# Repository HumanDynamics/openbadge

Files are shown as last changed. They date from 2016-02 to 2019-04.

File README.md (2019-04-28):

# OpenBadge project #

Welcome to the Open Badge project, an open-source framework and toolkit for measuring and shaping face-to-face social interactions using either custom hardware devices or smart phones, and real-time web-based visualizations. Open Badges is a modular system that allows researchers to monitor and collect interaction data from people engaged in real-life social settings. For more information, please read our main publications ([1](https://ieeexplore.ieee.org/document/8259434),[2](https://www.media.mit.edu/publications/rhythm-a-unified-measurement-platform-for-human-organizations/),[3](https://www.media.mit.edu/publications/open-badges-a-low-cost-toolkit-for-measuring-team-communication-and-dynamics/)) ,visit our [wiki](https://github.com/HumanDynamics/OpenBadge/wiki), or join our [discussion forum](https://groups.google.com/d/forum/rhythm-badges).

Additional repositories that are part of this project:
* https://github.com/mitmedialab/rhythm-badge-programmer - schematics, vector files and instructions for making a programming rig 

* https://github.com/HumanDynamics/openbadge-hub-py - a python based hub (base station) for pulling data from badges

* https://github.com/HumanDynamics/openbadge-hub - a Javascript/Cordova app that communicates with the badges and stores
 the data to a server
* https://github.com/HumanDynamics/openbadge-server - the backend server for the app

* https://github.com/HumanDynamics/openbadge-analysis - Python (2.7) package for loading and pre-processing badge data

* https://github.com/HumanDynamics/openbadge-analysis-examples - Examples showing how to use the analysis package

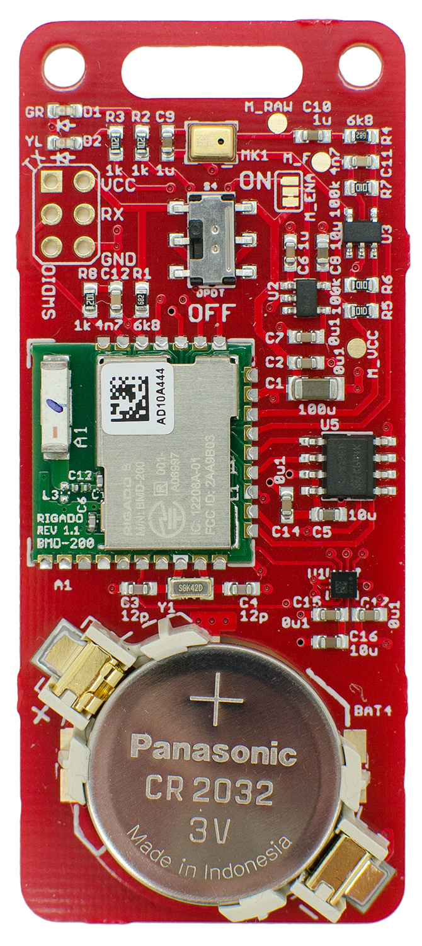
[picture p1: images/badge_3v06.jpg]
Badge Open Badge


## Docker wrapper ##
The nRF working environment is now available as a Docker container. The following commands have been tested under Ubuntu
linux, but should work under iOS as well (with some modifications, especially to the device names).

Important notes:
1. The badge must be connected to the programmer before starting the docker (using docker-compose run)
2. Docker will mount the project directory under /app inside the container, so the container can see the latest changes
 (no need to build the container after every code change)

Commands:
* docker-compose build : builds the docker container "nrf". You must run this command at least once before calling
 docker-compose run.
* docker-compose run nrf <COMMAND> : where <COMMAND> is a command to run inside the container.
  * When calling make (e.g. make badge_03v6_noDebug flashUnlock flashErase  flashS130 flashAPP), the script will automatically
  change the working directory to the data_collector directory. You can see the different make options by calling:
  "docker-compose run nrf make"
* docker-compose run nrf bash : opens an interactive bash shell
* ./programming_loop_docker.sh [test/prod] : a utility used for programming a batch of badges. It will compile once, and
 then enters a loop. Each time a new badge is placed, it will be automatically programmed and its MAC address will be
 written to the macs.log file. For most purposes, use the "prod" command variables. The "test" option turns on serial
 output and other testing features and is not recommended for production.

If you are using a raspberry pi to run this code, please use the raspberry pi compose file (-f docker-compose-raspi.yml). For example `docker-compose -f docker-compose-raspi.yml build`.

## Firmware testing tools ##
The framework includes two tools for testing firmware code
* Badge terminal. The utility opens a connections to a badge and allows you to run simple commands. To run, use the following docker command: `docker-compose run nrf terminal <MAC ADDRESS>`
* Integration tests. These are tests designed for testing basic badge functionality. To run the tests, use the following docker command: `docker-compose run nrf run_all_tests <MAC ADDRESS>`

Note that in order to run the integration tests, you'll need to have a badge connected with a serial interface. A regular J-Link debugger/programmer does not include these. We recommend using a nRF51 dev-kit as a programmer for this purpose (see our wiki/documentations on how to make one).

## Badge testing procedure ##
The badge firmware includes a tester mode that can be used for testing new badges. 
To compile, use the badge_03v6_tester flag (or badge_03v4_tester, for older hardware). For example:
```
make badge_03v6_noDebug flashUnlock flashErase  flashS130 flashAPP
```

Or, when using docker:
```
docker-compose run nrf make badge_03v6_noDebug flashUnlock flashErase  flashS130 flashAPP
```

Once programmed, the badge uses the LEDs to indicate the status of the test:
1. Blink red LED several times, one for each test (EEPROM, Flash, etc)
2. Microphone test. When it starts, both green and red LEDs will turn on 
It then looks for quiet->noise->quiet->noise pattern, each section must be at least 200 ms long. 
This must be completed within 10 seconds.
In a quiet place, simply say "ahhhh" twice, with pause in between. Every time the noise passed the threshold, the LEDs 
will turn off
3. Accelerometer test. When it starts, both green and red LEDs will turn on. Simply shake the badge
4. Once done, the green LED will turn off for several seconds and then turn off

Example for known issues with badge manufacturing:
* LEDs not turning on - might be a problem with the LEDs themselves
* When microphone test starts, both LEDs will momentarily turn on and then off
This might indicate a problem in the microphone filter or amplifier circuit (the microphone saturates and noise level says high)

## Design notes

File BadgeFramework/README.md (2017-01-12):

#BadgeFramework

This is a basic set of frameworks and libraries that are useful for interfacing with the badge in Python.

We currently have:

- BadgeConnection: An interface for an implementation of a badge communication layer.
- BLEBadgeConnection: An implementation of BadgeConnection that communicates with the badge over BLE using the Adafruit Bluefruit library.
- Badge: An object that communicates with a badge using the BadgeConnection
- badge_protocol: A set of BadgeMessage objects that make it easy to define, serialize, and deserialize the badge's proprietery binary communication messages.

We also include an example development terminal *terminal.py* that illustrates how one can use these various components to communicate with the badge. 

To try out the terminal, you must first install the [Adafruit Bluefruit library](https://github.com/adafruit/Adafruit_Python_BluefruitLE), and then simply run `python terminal.py` in this directory.

The purpose of this library is to expedite development of many tools (hub, integration test, developer terminal, etc.) that all have to communicate with the badge by forming a common, reusable codebase that all of these tools can use. As such, the framework is designed to be modular.  (E.g. the only portion of this framework that depends on a specific BLE library is BLEBadgeConnection, and one can easily swap out BadgeConnection implementations for say one that uses UART, or one can easily import the badge_protocol definitions into a different project)

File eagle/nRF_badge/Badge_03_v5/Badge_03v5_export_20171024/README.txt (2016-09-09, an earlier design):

Exported using PCB.ng CAM file
pnp_bom.txt file was created using the combine.py script and then cleaned up manually

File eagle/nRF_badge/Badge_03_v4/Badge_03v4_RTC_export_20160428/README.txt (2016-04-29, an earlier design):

In these files I manually fix the following issues i nthe BOM:
* C12 should be 4.7nF
* U4 should be 568-12405-1-ND 
* BAT1 should be BK-912-CT-ND (cut-tape)

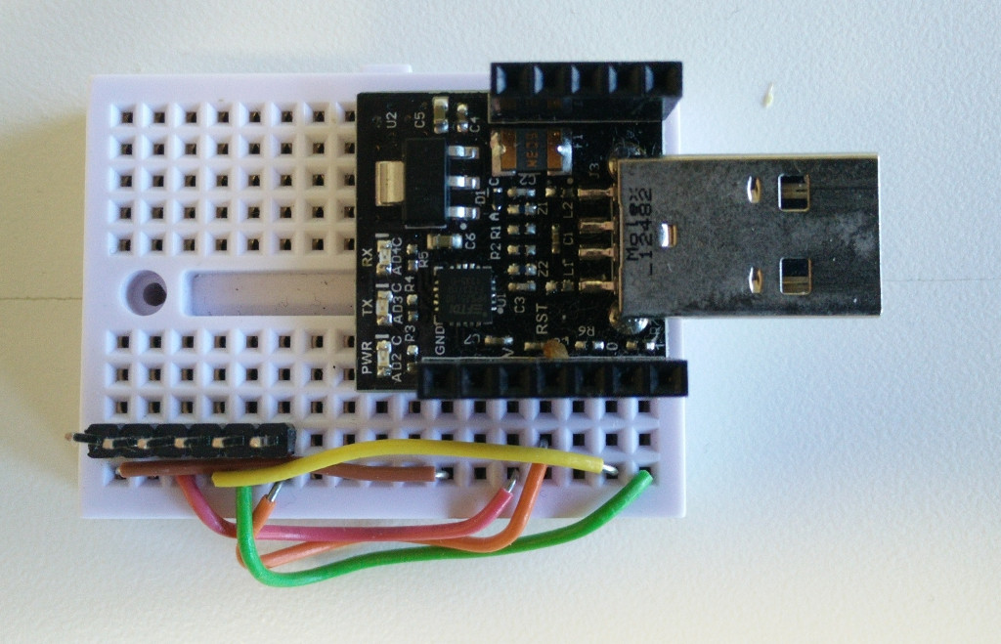
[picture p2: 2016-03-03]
images/v2_programmer.jpg

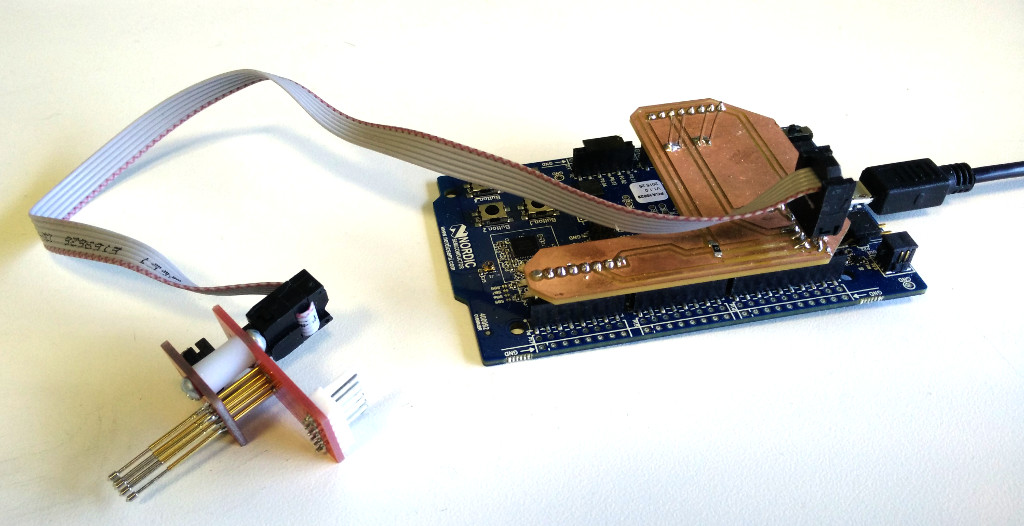
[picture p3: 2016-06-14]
images/programmer_v3.jpg

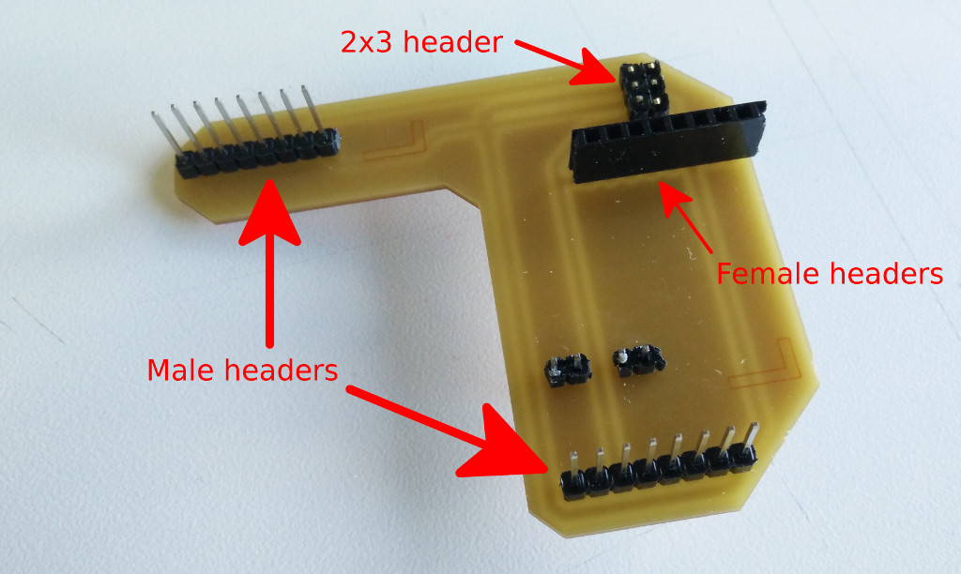
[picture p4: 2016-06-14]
images/programmer_v3_bottom.jpg

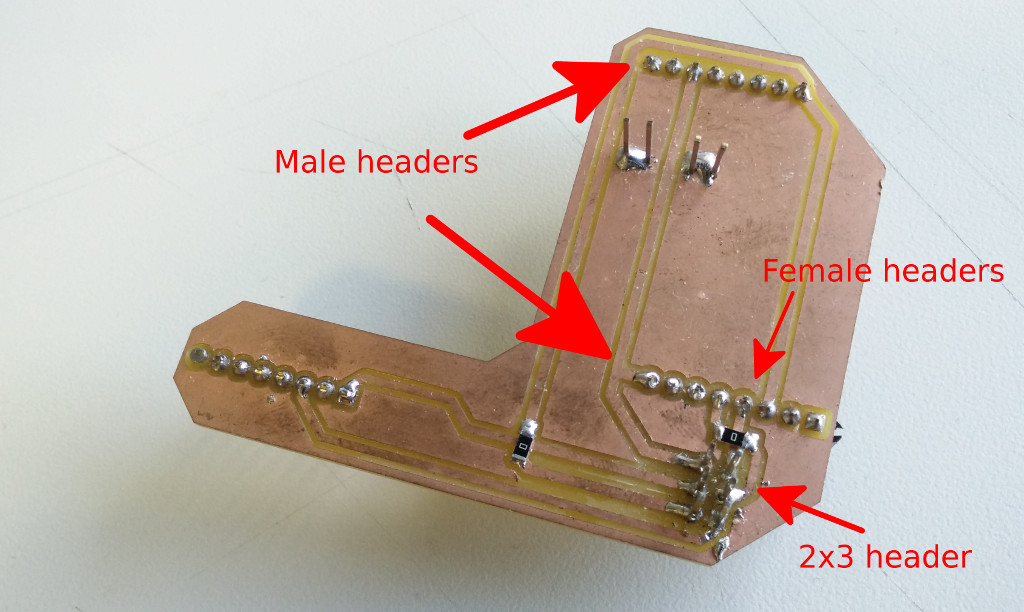
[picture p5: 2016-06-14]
images/programmer_v3_top.jpg

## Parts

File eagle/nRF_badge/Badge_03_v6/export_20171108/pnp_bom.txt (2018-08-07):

SMD component position file.
Centroid Data for pc board: "badge_03v6.brd" as of: 11/8/17 3:46 PM
Measurements are in mm. Comma delimited
Only surface mount components included

RefDes,LocationX,LocationY,Rotation,Layer,DigiKey
A1,9.500,36.500,90,Top,1604-1004-1-ND
BAT4,15.000,12.250,323,Top,BU2032SM-BT-GCT-ND
C1,23.000,41.500,0,Top,490-4539-1-ND
C2,22.250,43.500,0,Top,490-1532-1-ND
C3,9.250,26.000,180,Top,490-1405-1-ND
C4,17.250,26.000,0,Top,490-1405-1-ND
C5,24.000,31.750,0,Top,490-6405-1-ND
C6,21.000,52.000,90,Top,490-1543-1-ND
C7,22.250,45.500,0,Top,490-1532-1-ND
C8,23.500,52.000,90,Top,490-6405-1-ND
C9,11.500,60.500,90,Top,490-1543-1-ND
C10,22.750,61.000,0,Top,490-1543-1-ND
C11,26.500,59.000,180,Top,1276-1098-1-ND
C12,7.500,48.375,270,Top,1276-1098-1-ND
C14,20.750,32.500,90,Top,490-1532-1-ND
C15,27.250,26.000,0,Top,490-1532-1-ND
C16,26.000,28.125,0,Top,490-6405-1-ND
C17,24.250,26.000,180,Top,490-1532-1-ND
D1,3.500,63.000,0,Top,475-2709-1-ND
D2,3.500,60.500,0,Top,475-2712-1-ND
MK1,15.000,60.500,180,Top,423-1134-1-ND
R1,9.500,48.375,90,Top,RMCF0603JT6K80CT-ND
R2,9.500,60.500,270,Top,311-1.0KGRCT-ND
R3,7.500,60.500,270,Top,311-1.0KGRCT-ND
R4,26.500,61.000,180,Top,RMCF0603JT6K80CT-ND
R5,26.500,47.500,0,Top,311-100KGRCT-ND
R6,26.500,49.500,0,Top,311-100KGRCT-ND
R7,26.500,57.000,180,Top,311-100KGRCT-ND
R8,5.500,48.375,90,Top,311-1.0KGRCT-ND
R11,27.500,21.125,0,Top,311-1.0KGRCT-ND
R12,24.375,21.125,180,Top,311-1.0KGRCT-ND
S4,15.000,53.000,270,Top,401-2013-1-ND
U1,25.875,23.625,90,Top,497-14851-1-ND
U2,22.250,48.500,0,Top,296-18474-1-ND
U3,26.500,53.500,90,Top,MCP6231T-E/OTCT-ND
U5,25.500,35.500,180,Top,497-11405-1-ND
Y1,13.250,26.000,180,Top,535-11937-1-ND

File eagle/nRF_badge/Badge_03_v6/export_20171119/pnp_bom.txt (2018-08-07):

SMD component position file.
Centroid Data for pc board: "badge_03v6.brd" as of: 11/19/17 4:50 PM
Measurements are in mm. Comma delimited
Only surface mount components included

RefDes,LocationX,LocationY,Rotation,Layer,DigiKey
A1,9.500,36.500,90,Top,1604-1004-1-ND
BAT4,15.000,12.250,323,Top,BU2032SM-BT-GCT-ND
C1,23.000,41.500,0,Top,490-4539-1-ND
C2,22.250,43.500,0,Top,490-1532-1-ND
C3,9.250,26.000,180,Top,490-1405-1-ND
C4,17.250,26.000,0,Top,490-1405-1-ND
C5,24.000,31.750,0,Top,490-6405-1-ND
C6,21.000,52.000,90,Top,490-1543-1-ND
C7,22.250,45.500,0,Top,490-1532-1-ND
C8,23.500,52.000,90,Top,490-6405-1-ND
C9,11.500,60.500,90,Top,490-1543-1-ND
C10,22.750,61.000,0,Top,490-1543-1-ND
C11,26.500,59.000,180,Top,1276-1098-1-ND
C12,7.500,48.375,270,Top,1276-1098-1-ND
C14,20.750,32.500,90,Top,490-1532-1-ND
C15,24.125,24.000,180,Top,490-1532-1-ND
C16,24.125,21.875,180,Top,490-6405-1-ND
C17,27.125,24.000,0,Top,490-1532-1-ND
D1,3.500,63.000,0,Top,475-2709-1-ND
D2,3.500,60.500,0,Top,475-2712-1-ND
MK1,15.000,60.500,180,Top,423-1134-1-ND
R1,9.500,48.375,90,Top,RMCF0603JT6K80CT-ND
R2,9.500,60.500,270,Top,311-1.0KGRCT-ND
R3,7.500,60.500,270,Top,311-1.0KGRCT-ND
R4,26.500,61.000,180,Top,RMCF0603JT6K80CT-ND
R5,26.500,47.500,0,Top,311-100KGRCT-ND
R6,26.500,49.500,0,Top,311-100KGRCT-ND
R7,26.500,57.000,180,Top,311-100KGRCT-ND
R8,5.500,48.375,90,Top,311-1.0KGRCT-ND
S4,15.000,53.000,270,Top,401-2013-1-ND
U1,25.125,26.375,270,Top,497-14851-1-ND
U2,22.250,48.500,0,Top,296-18474-1-ND
U3,26.500,53.500,90,Top,MCP6231T-E/OTCT-ND
U5,25.500,35.500,180,Top,497-11405-1-ND
Y1,13.250,26.000,180,Top,535-11937-1-ND

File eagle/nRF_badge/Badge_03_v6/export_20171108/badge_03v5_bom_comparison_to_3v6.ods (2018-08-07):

v5 |  |  | v6
Part | Value | Digikey# | Part | Value | Digikey# | save value | same value | same key
A1 | BMD-200 | 1604-1004-1-ND | A1 | BMD-200 | 1604-1004-1-ND | 1 | 1 | 1
BAT4 | CR2032 | BU2032SM-BT-GCT-ND | BAT4 | CR2032 | BU2032SM-BT-GCT-ND | 1 | 1 | 1
C1 | 100u | 490-4539-1-ND | C1 | 100u | 490-4539-1-ND | 1 | 1 | 1
C2 | 0u1 | 490-1532-1-ND | C2 | 0u1 | 490-1532-1-ND | 1 | 1 | 1
C3 | 12p | 490-1405-1-ND | C3 | 12p | 490-1405-1-ND | 1 | 1 | 1
C4 | 12p | 490-1405-1-ND | C4 | 12p | 490-1405-1-ND | 1 | 1 | 1
C5 | 10u | 490-6405-1-ND | C5 | 10u | 490-6405-1-ND | 1 | 1 | 1
C6 | 1u | 490-1543-1-ND | C6 | 1u | 490-1543-1-ND | 1 | 1 | 1
C7 | 0u1 | 490-1532-1-ND | C7 | 0u1 | 490-1532-1-ND | 1 | 1 | 1
C8 | 10u | 490-6405-1-ND | C8 | 10u | 490-6405-1-ND | 1 | 1 | 1
C9 | 1u | 490-1543-1-ND | C9 | 1u | 490-1543-1-ND | 1 | 1 | 1
C10 | 1u | 490-1543-1-ND | C10 | 1u | 490-1543-1-ND | 1 | 1 | 1
C11 | 4n7 | 1276-1098-1-ND | C11 | 4n7 | 1276-1098-1-ND | 1 | 1 | 1
C12 | 4n7 | 1276-1098-1-ND | C12 | 4n7 | 1276-1098-1-ND | 1 | 1 | 1
C13 | 12p | 490-1405-1-ND |  |  |  | 0 | 0 | 0
C14 | 0u1 | 490-1532-1-ND | C14 | 0u1 | 490-1532-1-ND | 1 | 1 | 1
 |  |  | C15 | 0u1 | 490-1532-1-ND | 0 | 0 | 0
 |  |  | C16 | 10u | 490-6405-1-ND | 0 | 0 | 0
 |  |  | C17 | 0u1 | 490-1532-1-ND | 0 | 0 | 0
D1 | GR | 475-2709-1-ND | D1 | GR | 475-2709-1-ND | 1 | 1 | 1
D2 | YL | 475-2712-1-ND | D2 | YL | 475-2712-1-ND | 1 | 1 | 1
MK1 | SPU0414 | 423-1134-1-ND | MK1 | SPU0414 | 423-1134-1-ND | 1 | 1 | 1
R1 | 6k8 | RMCF0603JT6K80CT-ND | R1 | 6k8 | RMCF0603JT6K80CT-ND | 1 | 1 | 1
R2 | 1k | 311-1.0KGRCT-ND | R2 | 1k | 311-1.0KGRCT-ND | 1 | 1 | 1
R3 | 1k | 311-1.0KGRCT-ND | R3 | 1k | 311-1.0KGRCT-ND | 1 | 1 | 1
R4 | 6k8 | RMCF0603JT6K80CT-ND | R4 | 6k8 | RMCF0603JT6K80CT-ND | 1 | 1 | 1
R5 | 100k | 311-100KGRCT-ND | R5 | 100k | 311-100KGRCT-ND | 1 | 1 | 1
R6 | 100k | 311-100KGRCT-ND | R6 | 100k | 311-100KGRCT-ND | 1 | 1 | 1
R7 | 100k | 311-100KGRCT-ND | R7 | 100k | 311-100KGRCT-ND | 1 | 1 | 1
R8 | 1k | 311-1.0KGRCT-ND | R8 | 1k | 311-1.0KGRCT-ND | 1 | 1 | 1
R9 | 1k | 311-1.0KGRCT-ND |  |  |  | 0 | 0 | 0
R10 | 1k | 311-1.0KGRCT-ND |  |  |  | 0 | 0 | 0
 |  |  | R11 | 1k | 311-1.0KGRCT-ND | 0 | 0 | 0
 |  |  | R12 | 1k | 311-1.0KGRCT-ND | 0 | 0 | 0
S4 | DPDT | 401-2013-1-ND | S4 | DPDT | 401-2013-1-ND | 1 | 1 | 1
S2 | TACT6mm | CKN9087CT-ND |  |  |  | 0 | 0 | 0
 |  |  | U1 | LIS2DH12 | 497-14851-1-ND | 0 | 0 | 0
U2 | LP2985LV | 296-18474-1-ND | U2 | LP2985LV | 296-18474-1-ND | 1 | 1 | 1
U3 | MCP6231 | MCP6231T-E/OTCT-ND | U3 | MCP6231 | MCP6231T-E/OTCT-ND | 1 | 1 | 1
U4 | PCF85263 | 568-12405-1-ND |  |  |  | 0 | 0 | 0
U5 | M95M02 | 497-11405-1-ND | U5 | M95M02 | 497-11405-1-ND | 1 | 1 | 1
Y1 | 32768Hz | 535-11937-1-ND | Y1 | 32768Hz | 535-11937-1-ND | 1 | 1 | 1
Y2 | 32768Hz | 535-11937-1-ND

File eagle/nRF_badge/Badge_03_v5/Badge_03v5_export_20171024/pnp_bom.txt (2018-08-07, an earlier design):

SMD component position file.
Centroid Data for pc board: "badge_03v5.brd" as of: 10/24/17 2:08 PM
Measurements are in mm. Comma delimited
Only surface mount components included

RefDes,LocationX,LocationY,Rotation,Layer,DigiKey
A1,9.500,36.500,90,Top,1604-1004-1-ND
BAT4,15.000,12.250,323,Top,BU2032SM-BT-GCT-ND
C1,23.000,41.500,0,Top,490-4539-1-ND
C2,22.250,43.500,0,Top,490-1532-1-ND
C3,9.250,26.000,180,Top,490-1405-1-ND
C4,17.250,26.000,0,Top,490-1405-1-ND
C5,24.000,31.750,0,Top,490-6405-1-ND
C6,21.000,52.000,90,Top,490-1543-1-ND
C7,22.250,45.500,0,Top,490-1532-1-ND
C8,23.500,52.000,90,Top,490-6405-1-ND
C9,11.500,60.500,90,Top,490-1543-1-ND
C10,22.750,61.000,0,Top,490-1543-1-ND
C11,26.500,59.000,180,Top,1276-1098-1-ND
C12,7.500,48.375,270,Top,1276-1098-1-ND
C13,15.000,26.500,0,Bottom,490-1405-1-ND
C14,20.750,32.500,90,Top,490-1532-1-ND
D1,3.500,63.000,0,Top,475-2709-1-ND
D2,3.500,60.500,0,Top,475-2712-1-ND
MK1,15.000,60.500,180,Top,423-1134-1-ND
R1,9.500,48.375,90,Top,RMCF0603JT6K80CT-ND
R2,9.500,60.500,270,Top,311-1.0KGRCT-ND
R3,7.500,60.500,270,Top,311-1.0KGRCT-ND
R4,26.500,61.000,180,Top,RMCF0603JT6K80CT-ND
R5,26.500,47.500,0,Top,311-100KGRCT-ND
R6,26.500,49.500,0,Top,311-100KGRCT-ND
R7,26.500,57.000,180,Top,311-100KGRCT-ND
R8,5.500,48.375,90,Top,311-1.0KGRCT-ND
R9,15.000,41.750,0,Bottom,311-1.0KGRCT-ND
R10,15.000,39.500,0,Bottom,311-1.0KGRCT-ND
S2,24.500,25.750,0,Top,CKN9087CT-ND
S4,15.000,53.000,270,Top,401-2013-1-ND
U2,22.250,48.500,0,Top,296-18474-1-ND
U3,26.500,53.500,90,Top,MCP6231T-E/OTCT-ND
U4,15.000,34.500,90,Bottom,568-12405-1-ND
U5,25.500,35.500,180,Top,497-11405-1-ND
Y1,13.250,26.000,180,Top,535-11937-1-ND
Y2,15.000,28.750,0,Bottom,535-11937-1-ND

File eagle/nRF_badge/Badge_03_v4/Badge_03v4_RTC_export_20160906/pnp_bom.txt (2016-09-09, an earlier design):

SMD component position file.
Centroid Data for pc board: "badge_03v4.brd" as of: 9/6/16 6:49 PM
Measurements are in mm. Comma delimited
Only surface mount components included

RefDes,LocationX,LocationY,Rotation,Layer,DigiKey
A1,9.500,36.500,90,Top,1604-1004-1-ND
BAT1,15.000,12.250,0,Top,BK-912-CT-ND
C1,23.000,41.500,0,Top,490-4539-1-ND
C2,22.250,43.500,0,Top,490-1532-1-ND
C3,9.250,26.000,180,Top,490-1405-1-ND
C4,17.250,26.000,0,Top,490-1405-1-ND
C5,24.000,31.750,0,Top,490-6405-1-ND
C6,21.000,52.000,90,Top,490-1543-1-ND
C7,22.250,45.500,0,Top,490-1532-1-ND
C8,23.500,52.000,90,Top,490-6405-1-ND
C9,11.500,60.500,90,Top,490-1543-1-ND
C10,22.750,61.000,0,Top,490-1543-1-ND
C11,26.500,59.000,180,Top,1276-1098-1-ND
C12,7.500,48.375,270,Top,1276-1098-1-ND
C13,15.000,26.500,0,Bottom,490-1405-1-ND
C14,20.750,32.500,90,Top,490-1532-1-ND
D1,3.500,63.000,0,Top,475-2709-1-ND
D2,3.500,60.500,0,Top,475-2712-1-ND
MK1,15.000,60.500,180,Top,423-1134-1-ND
R1,9.500,48.375,90,Top,RMCF0603JT6K80CT-ND
R2,9.500,60.500,270,Top,311-1.0KGRCT-ND
R3,7.500,60.500,270,Top,311-1.0KGRCT-ND
R4,26.500,61.000,180,Top,RMCF0603JT6K80CT-ND
R5,26.500,47.500,0,Top,311-100KGRCT-ND
R6,26.500,49.500,0,Top,311-100KGRCT-ND
R7,26.500,57.000,180,Top,311-100KGRCT-ND
R8,5.500,48.375,90,Top,311-1.0KGRCT-ND
R9,15.000,41.750,0,Bottom,311-1.0KGRCT-ND
R10,15.000,39.500,0,Bottom,311-1.0KGRCT-ND
S1,15.000,53.000,0,Top,401-2002-1-ND
S2,24.500,25.750,0,Top,CKN9087CT-ND
U1,25.500,35.500,180,Top,AT25M02-SSHM-TCT-ND
U2,22.250,48.500,0,Top,296-18474-1-ND
U3,26.500,53.500,90,Top,MCP6231T-E/OTCT-ND
U4,15.000,34.500,90,Bottom,568-12405-1-ND
Y1,13.250,26.000,180,Top,535-11937-1-ND
Y2,15.000,28.750,0,Bottom,535-11937-1-ND

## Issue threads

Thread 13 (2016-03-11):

HumanDynamics/openbadge #13: nRF badge skips time

OrenLederman, 2016-03-11:
Badge time jumped to the future. This does not seem to be an hardware issue (battery level was within reason)

**Data file**, date skipped from 2016-03-10 to 2016-04-28
2016-03-10 22:20:34,2.56891489029,250,1,1,1,1,1,1,1,1,1,1,1,1,1,1,1,1,1,1,1,1,1,1,1,1,1,1,1,1,1,1,1,1,1,1,1,1,1,1,1,1,1,1,1,1,1,1,1,1,1,1,1,1,1,1,1,1,1,1,1,1,1,1,2,1,1,1,1,1,1,1,1,1,1,1,1,1,1,1,1,1,1,1,1,1,1,1,1,1,1,1,1,1,1,1,1,1,1,1,1,1,1,1,1,1,1,1,1,1,1,1,1,1,1,1,1,1
2016-04-28 03:59:43,2.60410547256,250,1,1,1,1,1,1,1,1,1,1,1,1,1,1,1,1,1,1,1,1,1,1,1,1,1,1,1,1,1,1,1,1,1,1,1,1,1,1,1,1,1,1,1,1,1,1,1,1,1,1,1,1,1,1,1,1,1,1,1,1,1,1,1,1,1,1,2,1,1,1,1,1,1,1,1,1,1,1,1,1,1,1,1,1,1,1,1,1,1,1,1,1,1,1,1,1,1,1,1,1,1,1,1,1,1,1,1,1,1,1,1,1,1,1,1,1

**server log**, did not send a new date in between
2016-03-10 22:21:37,858 - INFO - [D1:61:D8:00:57:61] Talking with D1:61:D8:00:57:61
2016-03-10 22:21:39,416 - INFO - [D1:61:D8:00:57:61] Connected
2016-03-10 22:21:39,543 - INFO - [D1:61:D8:00:57:61] Got status
2016-03-10 22:21:39,557 - INFO - [D1:61:D8:00:57:61] Already synced
2016-03-10 22:21:39,560 - INFO - [D1:61:D8:00:57:61] Requesting data...
2016-03-10 22:21:40,837 - INFO - [D1:61:D8:00:57:61] Waiting for more data...
2016-03-10 22:21:41,843 - INFO - [D1:61:D8:00:57:61] Waiting for more data...
2016-03-10 22:21:42,847 - INFO - [D1:61:D8:00:57:61] Waiting for more data...
2016-03-10 22:21:42,851 - INFO - [D1:61:D8:00:57:61] finished reading data
2016-03-10 22:21:42,869 - INFO - [D1:61:D8:00:57:61] disconnected
2016-03-10 22:21:42,872 - INFO - [D1:61:D8:00:57:61] Chunks received: 1
2016-03-10 22:21:42,876 - INFO - [D1:61:D8:00:57:61] saving chunks to file
2016-03-10 22:21:42,879 - INFO - [D1:61:D8:00:57:61] Chunk timestamp: 2016-03-10 22:20:34, Voltage: 2.56891489029, Samples in chunk: 116
2016-03-10 22:21:42,888 - INFO - [D1:61:D8:00:57:61] done writing
2016-03-10 22:21:44,899 - INFO - [None] Reading whitelist:
2016-03-10 22:21:44,904 - INFO - [None]     D1:61:D8:00:57:61
2016-03-10 22:21:44,907 - INFO - [None]     EC:21:82:A8:0B:59
2016-03-10 22:21:44,911 - INFO - [None] Scanning for devices...
2016-03-10 22:21:49,924 - DEBUG - [None] Found EC:21:82:A8:0B:59, added
2016-03-10 22:21:49,928 - DEBUG - [None] Found D1:61:D8:00:57:61, added
2016-03-10 22:21:49,931 - INFO - [None] Found: 2 devices
2016-03-10 22:21:51,935 - INFO - [None] Communicating with synced devices...
...
2016-03-10 22:21:59,312 - INFO - [D1:61:D8:00:57:61] Talking with D1:61:D8:00:57:61
2016-03-10 22:22:00,825 - INFO - [D1:61:D8:00:57:61] Connected
2016-03-10 22:22:00,963 - INFO - [D1:61:D8:00:57:61] Got status
2016-03-10 22:22:00,967 - INFO - [D1:61:D8:00:57:61] Already synced
2016-03-10 22:22:00,979 - INFO - [D1:61:D8:00:57:61] disconnected
2016-03-10 22:22:00,982 - INFO - [D1:61:D8:00:57:61] No data ready
2016-03-10 22:22:02,988 - INFO - [None] Reading whitelist:
2016-03-10 22:22:03,002 - INFO - [None]     D1:61:D8:00:57:61
2016-03-10 22:22:03,016 - INFO - [None]     EC:21:82:A8:0B:59
2016-03-10 22:22:03,019 - INFO - [None] Scanning for devices...
2016-03-10 22:22:08,064 - DEBUG - [None] Found EC:21:82:A8:0B:59, added
2016-03-10 22:22:08,078 - DEBUG - [None] Found D1:61:D8:00:57:61, added
2016-03-10 22:22:08,088 - INFO - [None] Found: 2 devices
2016-03-10 22:22:10,093 - INFO - [None] Communicating with synced devices...
...
2016-03-10 22:22:13,499 - INFO - [D1:61:D8:00:57:61] Talking with D1:61:D8:00:57:61
2016-03-10 22:22:15,666 - INFO - [D1:61:D8:00:57:61] Connected
2016-03-10 22:22:15,803 - INFO - [D1:61:D8:00:57:61] Got status
2016-03-10 22:22:15,807 - INFO - [D1:61:D8:00:57:61] Already synced
2016-03-10 22:22:15,810 - INFO - [D1:61:D8:00:57:61] Requesting data...
2016-03-10 22:22:17,088 - INFO - [D1:61:D8:00:57:61] Waiting for more data...
2016-03-10 22:22:18,092 - INFO - [D1:61:D8:00:57:61] Waiting for more data...
2016-03-10 22:22:19,097 - INFO - [D1:61:D8:00:57:61] Waiting for more data...
2016-03-10 22:22:19,101 - INFO - [D1:61:D8:00:57:61] finished reading data
2016-03-10 22:22:19,138 - INFO - [D1:61:D8:00:57:61] disconnected
2016-03-10 22:22:19,142 - INFO - [D1:61:D8:00:57:61] Chunks received: 1
2016-03-10 22:22:19,155 - INFO - [D1:61:D8:00:57:61] saving chunks to file
2016-03-10 22:22:19,159 - INFO - [D1:61:D8:00:57:61] Chunk timestamp: 2016-04-28 03:59:43, Voltage: 2.60410547256, Samples in chunk: 116
2016-03-10 22:22:19,174 - INFO - [D1:61:D8:00:57:61] done writing

OrenLederman, 2016-03-12:
for reference, here's the first line from the log (so you'll know how long it was up):
2016-03-09 09:56:51,3.12492656708,250,1,1,1,1,1,1,1,1,1,1,1,1,1,1,1,1,1,1,1,1,1,1,1,1,1,1,1,1,1,1,1,1,1,1,1,1,1,1,4,2,1,1,1,1,1,1,1,1,1,1,1,1,1,1,1,1,1,1,1,1,1,1,1,1,1,1,1,1,1,1,1,1,1,1,1,1,1,1,1,1,1,1,1,1,1,1,1,1,1,1,1,1,1,1,1,2,1,2,1,2,2,9,1,1,1,1,1,1,1,1,1,1,1,1,1,1

OrenLederman, 2016-03-12:
The problem appeared in a second badge as well. With the second badge, the RasPI crashed in the middle of the test (after 1.5 days). The logs before the scan shows the correct date, the logs right after the crash shows the faulty date. 

I find it hard to believe that the crashed caused it, or that these two problems happened at the same time. I think that something in timekeeping of the badge changed. Perhaps we manipulate the date before sending it out to the server, and the stored data is actually correct?

OrenLederman, 2016-03-16:
another example
2016-03-12 10:52:12,2.95249271393,250,1,1,1,1,1,1,1,1,1,1,1,1,1,1,1,1,1,1,1,1,1,1,1,1,1,1,2,1,1,1,1,1,1,1,1,1,1,1,1,1,1,1,1,1,1,1,1,1,1,1,1,1,1,1,1,1,1,1,1,1,1,1,1,1,1,1,1,1,1,1,1,1,1,1,1,1,1,1,1,1,1,1,1,1,1,1,1,1,1,1,1,1,1,1,1,1,1,1,1,1,1,1,1,1,1,1,1,1,1,1,1,1,1,1,1,1
...
2016-03-14 00:17:51,2.68504405022,250,1,1,1,1,1,1,1,1,1,1,1,1,1,1,1,1,1,1,1,1,1,1,1,1,1,1,1,1,1,1,1,1,1,1,1,1,1,1,1,1,1,1,1,1,1,1,1,1,1,1,1,1,1,1,1,1,1,1,1,1,1,1,1,1,1,1,1,1,1,1,1,1,1,1,1,1,1,1,1,1,1,1,1,1,1,1,1,1,1,1,1,1,1,1,1,1,1,1,1,1,1,1,1,1,1,1,1,1,1,1,1,1,1,1,1,1
2016-05-01 04:57:00,2.67800593376,250,1,1,1,1,1,1,1,1,1,1,1,1,1,1,1,1,1,1,1,1,1,1,1,1,1,1,1,1,1,1,1,1,1,1,1,1,1,1,1,1,1,1,1,1,1,1,1,1,1,1,1,1,1,1,1,1,1,1,1,1,1,1,1,1,1,1,1,1,1,1,1,1,1,1,1,1,1,1,1,1,1,1,1,1,1,1,1,1,1,1,1,1,1,1,1,1,1,1,1,1,1,1,1,1,1,1,1,1,1,1,1,1,1,1,1,1

anguslocke, 2016-03-16:
For the two bug instances above:

-Seconds elapsed between first chunk and chunk just before time jump:
131,023; 134,739
^^^ Accounting for DST (3600s), within ~2mins.  i.e. the error probably happened the same elapsed time from power-on (one badge just got synced 2mins later).
Maybe 2^17 = 131,072?

-Length of time jump, in seconds:
4,163,949;  4,167,549
^^^ Accounting for DST (3600s), the jumps are exactly the same length.
related to 2^22 = 4,194,304?

OrenLederman, 2016-03-17:
FYI - if the server re-sends the datetime to the badge it uses the new date. Not sure if this information helps.

closed 2016-04-06 by OrenLederman

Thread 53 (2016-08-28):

HumanDynamics/openbadge #53: Badge sometimes send old chunks or empty chunks

OrenLederman, 2016-08-28:
I noticed that the badge sometimes send data older than the timestamp we ask for. In fact, it seems to does that when:

1. After the badge reset and recording hasn't been started yet it will send an empty chunk (timestamp = 0)

2. After the badge stopped recording, it will send a date from some recent chunk, even if it's earlier than the time requested (see example log below)

Be careful if you decide to change anything in this mechanism.. if it's not something very obvious we'll might need to just keep it as an open bug

One workaround, is to start recording before pulling new data. In fact,t hat is what we do with the phone hub, which might explain why we haven't noticed this before.

Example:

2016-08-28 11:16:27,789 - INFO - Resetting BLE
2016-08-28 11:16:29,801 - INFO - Done resetting BLE
2016-08-28 11:16:29,801 - INFO - Started
2016-08-28 11:16:29,802 - INFO - Will request data since 1472397389.000000
2016-08-28 11:16:29,802 - INFO - Scanning for devices...
2016-08-28 11:16:29,802 - INFO - Reading whitelist:
2016-08-28 11:16:29,805 - INFO -     F9:A0:3E:12:9E:3E
2016-08-28 11:16:32,823 - DEBUG - Found E7:00:28:A7:DB:C2, but not on whitelist. Device info: {'rssi': -68, 'scan_date': datetime.datetime(2016, 8, 28, 11, 16, 32, 822945), 'adv_payload': {'proximity_status': 0, 'sync_status': 0, 'audio_status': 0, 'mac': [231, 0, 40, 167, 219, 194], 'badge_id': 63880, 'voltage': 2.75, 'status_flags': 0, 'project_id': 0}}
2016-08-28 11:16:32,824 - DEBUG - Found F9:A0:3E:12:9E:3E, added. Device info: {'rssi': -78, 'scan_date': datetime.datetime(2016, 8, 28, 11, 16, 32, 823176), 'adv_payload': {'proximity_status': 0, 'sync_status': 1, 'audio_status': 0, 'mac': [249, 160, 62, 18, 158, 62], 'badge_id': 830, 'voltage': 2.7, 'status_flags': 1, 'project_id': 0}}
2016-08-28 11:16:34,826 - DEBUG - Unseen device. Adding to dict: F9:A0:3E:12:9E:3E
2016-08-28 11:16:34,827 - INFO - [F9:A0:3E:12:9E:3E] Connecting to F9:A0:3E:12:9E:3E
2016-08-28 11:16:36,092 - INFO - [F9:A0:3E:12:9E:3E] Connected
2016-08-28 11:16:36,302 - INFO - [F9:A0:3E:12:9E:3E] Got status
2016-08-28 11:16:36,302 - INFO - [F9:A0:3E:12:9E:3E] Badge datetime was: 1472397396,111, Voltage: 2.70615839958
2016-08-28 11:16:36,302 - INFO - [F9:A0:3E:12:9E:3E] Requesting data since 1472397389 802.085
2016-08-28 11:16:36,443 - INFO - [F9:A0:3E:12:9E:3E] finished reading data
2016-08-28 11:16:36,443 - INFO - [F9:A0:3E:12:9E:3E] Requesting scans since 1472397389
2016-08-28 11:16:36,589 - INFO - [F9:A0:3E:12:9E:3E] finished reading data
2016-08-28 11:16:36,589 - DEBUG - [F9:A0:3E:12:9E:3E] Setting last seen audio chunk to 1472396577.994
2016-08-28 11:16:36,589 - INFO - [F9:A0:3E:12:9E:3E] Disconnecting from F9:A0:3E:12:9E:3E
2016-08-28 11:16:36,591 - INFO - Successfully pulled data
2016-08-28 11:16:36,591 - INFO - Chunks received: 1
2016-08-28 11:16:36,591 - INFO - saving chunks to file
2016-08-28 11:16:36,591 - INFO - CSV: Chunk timestamp: 1472396578.994, Voltage: 2.67448687553, Delay: 50, Samples in chunk: 0
2016-08-28 11:16:36,591 - INFO - done writing
2016-08-28 11:16:36,591 - INFO - No proximity scans ready
2016-08-28 11:16:38,594 - INFO - Sleeping...
2016-08-28 11:16:44,600 - INFO - Scanning for devices...
2016-08-28 11:16:44,601 - INFO - Reading whitelist:
2016-08-28 11:16:44,601 - INFO -     F9:A0:3E:12:9E:3E
2016-08-28 11:16:47,731 - DEBUG - Found E7:00:28:A7:DB:C2, but not on whitelist. Device info: {'rssi': -72, 'scan_date': datetime.datetime(2016, 8, 28, 11, 16, 47, 731034), 'adv_payload': {'proximity_status': 0, 'sync_status': 0, 'audio_status': 0, 'mac': [231, 0, 40, 167, 219, 194], 'badge_id': 63880, 'voltage': 2.75, 'status_flags': 0, 'project_id': 0}}
2016-08-28 11:16:47,731 - DEBUG - Found F9:A0:3E:12:9E:3E, added. Device info: {'rssi': -76, 'scan_date': datetime.datetime(2016, 8, 28, 11, 16, 47, 731212), 'adv_payload': {'proximity_status': 0, 'sync_status': 1, 'audio_status': 0, 'mac': [249, 160, 62, 18, 158, 62], 'badge_id': 830, 'voltage': 2.67, 'status_flags': 1, 'project_id': 0}}
2016-08-28 11:16:49,733 - INFO - [F9:A0:3E:12:9E:3E] Connecting to F9:A0:3E:12:9E:3E
2016-08-28 11:16:51,002 - INFO - [F9:A0:3E:12:9E:3E] Connected
2016-08-28 11:16:51,142 - INFO - [F9:A0:3E:12:9E:3E] Got status
2016-08-28 11:16:51,142 - INFO - [F9:A0:3E:12:9E:3E] Badge datetime was: 1472397410,932, Voltage: 2.67448687553
2016-08-28 11:16:51,143 - INFO - [F9:A0:3E:12:9E:3E] Requesting data since 1472396577 994
2016-08-28 11:16:56,253 - INFO - [F9:A0:3E:12:9E:3E] finished reading data
2016-08-28 11:16:56,254 - INFO - [F9:A0:3E:12:9E:3E] Requesting scans since 1472397389
2016-08-28 11:16:56,392 - INFO - [F9:A0:3E:12:9E:3E] finished reading data
2016-08-28 11:16:56,392 - DEBUG - [F9:A0:3E:12:9E:3E] Setting last seen audio chunk to 1472396686.322
2016-08-28 11:16:56,393 - INFO - [F9:A0:3E:12:9E:3E] Disconnecting from F9:A0:3E:12:9E:3E
2016-08-28 11:16:56,393 - INFO - Successfully pulled data
2016-08-28 11:16:56,393 - INFO - Chunks received: 20
2016-08-28 11:16:56,394 - INFO - saving chunks to file
2016-08-28 11:16:56,394 - INFO - CSV: Chunk timestamp: 1472396578.994, Voltage: 2.67448687553, Delay: 50, Samples in chunk: 114
2016-08-28 11:16:56,394 - INFO - CSV: Chunk timestamp: 1472396584.694, Voltage: 2.67448687553, Delay: 50, Samples in chunk: 114
2016-08-28 11:16:56,394 - INFO - CSV: Chunk timestamp: 1472396590.395, Voltage: 2.67448687553, Delay: 50, Samples in chunk: 114
2016-08-28 11:16:56,394 - INFO - CSV: Chunk timestamp: 1472396596.095, Voltage: 2.67448687553, Delay: 50, Samples in chunk: 114
2016-08-28 11:16:56,395 - INFO - CSV: Chunk timestamp: 1472396601.796, Voltage: 2.67448687553, Delay: 50, Samples in chunk: 114
2016-08-28 11:16:56,395 - INFO - CSV: Chunk timestamp: 1472396607.496, Voltage: 2.67448687553, Delay: 50, Samples in chunk: 114
2016-08-28 11:16:56,395 - INFO - CSV: Chunk timestamp: 1472396613.197, Voltage: 2.67448687553, Delay: 50, Samples in chunk: 114
2016-08-28 11:16:56,395 - INFO - CSV: Chunk timestamp: 1472396618.897, Voltage: 2.67448687553, Delay: 50, Samples in chunk: 114
2016-08-28 11:16:56,395 - INFO - CSV: Chunk timestamp: 1472396624.597, Voltage: 2.67448687553, Delay: 50, Samples in chunk: 114
2016-08-28 11:16:56,396 - INFO - CSV: Chunk timestamp: 1472396630.321, Voltage: 2.67448687553, Delay: 50, Samples in chunk: 114
2016-08-28 11:16:56,396 - INFO - CSV: Chunk timestamp: 1472396636.021, Voltage: 2.67448687553, Delay: 50, Samples in chunk: 114
2016-08-28 11:16:56,396 - INFO - CSV: Chunk timestamp: 1472396641.721, Voltage: 2.67448687553, Delay: 50, Samples in chunk: 114
2016-08-28 11:16:56,396 - INFO - CSV: Chunk timestamp: 1472396647.422, Voltage: 2.67448687553, Delay: 50, Samples in chunk: 114

anguslocke, 2016-08-29:
Fixed in newScans branch.

anguslocke, 2016-08-29:
At the start of your included logs:

> 2016-08-28 11:16:27,789 - INFO - Resetting BLE
2016-08-28 11:16:29,801 - INFO - Done resetting BLE
2016-08-28 11:16:29,801 - INFO - Started
2016-08-28 11:16:29,802 - INFO - Will request data since **1472397389.000000**

Near the end:

> 2016-08-28 11:16:49,733 - INFO - [F9:A0:3E:12:9E:3E] Connecting to F9:A0:3E:12:9E:3E
2016-08-28 11:16:51,002 - INFO - [F9:A0:3E:12:9E:3E] Connected
2016-08-28 11:16:51,142 - INFO - [F9:A0:3E:12:9E:3E] Got status
2016-08-28 11:16:51,142 - INFO - [F9:A0:3E:12:9E:3E] Badge datetime was: 1472397410,932, Voltage: 2.67448687553
2016-08-28 11:16:51,143 - INFO - [F9:A0:3E:12:9E:3E] Requesting data since **1472396577** 994
2016-08-28 11:16:56,253 - INFO - [F9:A0:3E:12:9E:3E] finished reading data
2016-08-28 11:16:56,254 - INFO - [F9:A0:3E:12:9E:3E] Requesting scans since 1472397389
2016-08-28 11:16:56,392 - INFO - [F9:A0:3E:12:9E:3E] finished reading data
2016-08-28 11:16:56,392 - DEBUG - [F9:A0:3E:12:9E:3E] Setting last seen audio chunk to 1472396686.322
2016-08-28 11:16:56,393 - INFO - [F9:A0:3E:12:9E:3E] Disconnecting from F9:A0:3E:12:9E:3E
2016-08-28 11:16:56,393 - INFO - Successfully pulled data
2016-08-28 11:16:56,393 - INFO - Chunks received: 20
2016-08-28 11:16:56,394 - INFO - saving chunks to file
2016-08-28 11:16:56,394 - INFO - CSV: Chunk timestamp: **1472396578**.994, Voltage: 2.67448687553, Delay: 50, Samples in chunk: 114
2016-08-28 11:16:56,394 - INFO - CSV: Chunk timestamp: 1472396584.694, Voltage: 2.67448687553, Delay: 50, Samples in chunk: 114

The badge _is_ in fact sending what the server asked for.
It's the _server_ that jumped back to an earlier time.  So this is either a server bug, or an issue that arose from the bad empty chunks the badge sent.  (the empty chunks issue is fixed now)

anguslocke, 2016-08-29:
Yep, that's what happened.  The badge sent the bad empty chunk, which had some undefined timestamp.  And the server updated last_audio_ts to that bad timestamp.  (minus 1 second)
So it appears the empty chunk fix solves both issues?

closed 2016-08-29 by anguslocke

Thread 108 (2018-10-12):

HumanDynamics/openbadge #108: Clarifications before fabricating badges

patcon, 2018-10-12:
First off, thank you so so much for making this repo public and keeping it up-to-date. I've had such energizing conversations with people about working with the artifacts of your project.

### Context

I'm just getting ready to order some badges in unofficial collaboration with @shuyanglin of [PDIS](https://pdis.nat.gov.tw/en/), the Taiwanese government's digital innovation department created by [Digital Minister Audrey Tang](https://qz.com/767298/taiwans-new-digital-minister-is-a-transgender-software-programmer-who-wants-to-make-government-more-open/).

We're currently getting ready to order a pilot batch of 15 sociometric badges and 3 BLE beacons. We'll later order 85 more, for use at a civic hackathon and other loose experiments. The pilot and larger scale experiment will likely have two separate goals:

1. to take certain online processes into physical space (pilot), and
2. to help the civic tech community better understand itself (larger experiment)

### Disclaimer

I don't have hardware experience myself. I'm eagerly collaborating with people like @kevinphy of Taipei Hackerspace. Having said that, I accept full responsibility for any stupid questions I ask in this issue :)

### Questions

#### Circuit Board Fabrication

1. Are the newest files exports always the ones you'd recommend? (I will be assuming "yes" with my following links and questions, but please advise if incorrect. I can imagine considerations of stability vs bleeding edge, but I'm not clear how to account for that.)
2. Will we need to order/build our own "programmer"? Could we manage without? Is this [all the details](https://github.com/HumanDynamics/openbadge/tree/master/eagle/nRF_badge/Badge_03v2-Prog) for doing that?
3. What is the difference between [`Badge_03_v6`](https://github.com/HumanDynamics/openbadge/tree/master/eagle/nRF_badge/Badge_03_v6) and [`Badge_03_v6_LIS2DH12_breakout`](https://github.com/HumanDynamics/openbadge/tree/master/eagle/nRF_badge/Badge_03_v6_LIS2DH12_breakout)? Which is recommended? These are the facts as I see them in relation to this question:
    - :mag: All the export dirs in v6 have BOMs, but v6_LIS2DH12 lacks a BOM
    - :mag: The files were all committed at the same time, so no clues there.
    - :mag: all the BOMs in v6 exports actually have the LIS2DH12 component (3-axis accelerometer) included [(example)](https://github.com/HumanDynamics/openbadge/blob/master/eagle/nRF_badge/Badge_03_v6/export_20171108/badge_03v6_bom.csv)
4. Will `Badge_03v2-Prog` (assuming this is the programmer device), work with more recent v6 badges?

#### Misc.

1. Which BLE beacons would you recommend?

We'll be happy to contribute back what we learn by expanding on the documentation in this repo!

## Note

I emailed David Shrier before arriving in Taiwan, in relation to my hopes of running a sociometric badge experiment. He responded quickly and graciously, and tried to point me in the right direction, but it seemed the direction was away from the badges, which is the primary interest. Apologies for any confusion this second outreach causes :)

OrenLederman, 2018-10-12:
These are all good question.

1. The newest export is the right one to use (we've made ~200 units using this design so far). https://github.com/HumanDynamics/openbadge/tree/master/eagle/nRF_badge/Badge_03_v6/export_20180201 

2. You'll need to make your own programmer. The link you mentioned has the design itself. It has a very simple design - order the board from any PCB maker, and solder the headers yourself (the LED is optional). You'll need a few more parts though. There is more information on that here - https://github.com/HumanDynamics/openbadge/wiki/Open-Badge-V3.0#building-a-programmer (note - you don't have to make the programming frame/rig, just get the pogo-pin pkit from sparkfun)

3. Ignore Badge_03_v6_LIS2DH12_breakout. It was just a test

4. Yes, this programmer will work for all versions of the badge

5. I actually never really used BLE beacons - I always use my badges as location beacons. It gives me more flexibility. also, the new version of the server+hub allows you to program them remotely (which saves time). If you do get BLE beacons, make sure they support the iBeacons protocol. You'll need to manually set their IDs using the program that comes with them. In the past, I used beacons from these companies https://store.radiusnetworks.com/  and https://estimote.com/

A couple of notes about fabrication - the fabrication is straight forward, but different PCBAs have different equipment. In our case, the company had to use small glue dots to keep the passives (capacitors and resistors) in place so they don't "tombstone".

patcon, 2018-10-13:
@OrenLederman, you are my hero. I'll process this new info with our group, and we'll keep this issue updated with progress. (I'll create new issues for any specific code/doc contributions.)

patcon, 2018-10-25:
Any recommendations on whether to even attempt surface-mount soldering on this board?

I'm [reading this article](https://hackaday.com/2016/03/17/so-youre-scared-of-surface-mount/), and trying to decide if these components are small enough that a novice should avoid, even to save a little assembly money. I'm seeing some 0603 size parts, which I think might be too small. Curious your advice, or whether anyone on your team did anything but pick-and-place. Thanks! :)

OrenLederman, 2018-11-08:
Keeping this thread open until we document this somewhere

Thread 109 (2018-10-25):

HumanDynamics/openbadge #109: Host project on community website for easier ordering

patcon, 2018-10-25:
Hi again @OrenLederman!

A few of us have been talking and meeting to work on this. (We keep [notes](https://hackmd.io/s/H1mc0oj9Q#Meetings) fwiw)

We came across some websites that we were hoping to use so that it's simpler for the next group to walk this path. They allow for project sharing, and essentially one-click ordering for others who want to do the same fabrication.

- [PCBWay: Shared Projects](https://www.pcbway.com/project/)
- [seeed studio: Project Hub](https://project.seeedstudio.com/)
- [Elecrow: Cooperated Designers](https://www.elecrow.com/cooperated-designers) (seems more profit-motivated and top-down than others)

*Would you be opposed to openbadge having a presence on community platforms like this?

Here are some comments -- 🔍  facts, ❤️ feelings, and 💡 ideas -- related to this discussion:

_community platforms:_ Meaning community side of PCBWay, seeed studios, etc.

#### General

1. :mag: The openbadge license is MIT, and so we're technically free to do anything.
1. :heart: I feel preference to work in a way that aligns with your expectations and goals.
1. :heart: I feel eager to make it simpler for others to start projects with openbadge.
1. :heart: I feel eager to actively contribute to having a presence on community platforms, so that I can help foster a larger peer community of collaborators.
1. :heart: I feel open to letting your team manage this, if you have strong feelings on it.
1. :mag: The community platforms don't seem to offer accounts for team management.
1. :bulb: We could share an single account.
1. :mag: seeed studio has [some options for teams/contributors](https://project.seeedstudio.com/guidelines) that we could use accordingly.

#### Profit-sharing and incentivization on platforms

1. :mag: The platforms seem to offer financial incentives (paid or discount).
1. :heart: I feel uninterested in being personally enriched by hosting a project on these platforms.
1. :heart: I feel that the incentive could be used to promote something community-minded.
1. :bulb: We could enabled "monetization", but use it to give community projects discounts/credits.
1. :bulb: Alternatively, we could try to disable any monetization on the account.
1. :heart: I feel that monetization should be disabled if it in any way increases the price of regular orders.
1. :mag: I've [tweeted](https://twitter.com/patconnolly/status/1055375819437047808) at PCBWay to discover options for commission.
1. :mag: The community platforms have referral programs, eg [PCBWay's](https://www.pcbway.com/helpcenter/promotions/How_does_the_referral_program_work_.html?search=).
    1. :bulb: We could use the above-mentioned shared account to receive referral bonuses from doc/readme links, and hold it for community uses.

Anyhow, I look forward to hearing your thoughts! Hopefully this is a helpful format for this discussion :)

cc: @kevinphys (pls feel free to add your own thoughts! 😄 )

OrenLederman, 2018-10-25:
Hi guys,

(also adding @jordanreedie  and @MichaelHopfengaertner to the discussion)

I think it's a great idea, and will be happy to help. I was playing with the idea of trying order badges from PCBWay or Seeedstudio so I can make the assembly process more generic and easy for people. We are getting many requests for badges, so it can be a good way for enabling people to make their own. 

Monetization might be a good idea. I'm not planning to get rich because of this project, but this money can help support some more development of the system and benefit the community (for example, designing a badge firmware "burning" tool that is easier to use...).

The only thing is that I currently don't have time to take lead on this (trying to wrap up my PhD this year, and handling a 2mo baby and a 2yo toddler..). But I will help with whatever I can. If there is enough interest, I might be able to pull in some more resources (students) to help.

Oh, also - we should refer to the project as Rhythm Badge (OpenBadge is an official Mozilla project, and they asked us to change the name). At some point i'll rename the repositories...

Also - fun fact - we have a new firmware version in the making (in a fork of the project). A complete re-write that will make it easier for people to contribute to the project. We are almost done testing all the existing functionality, and will soon start testing some new stuff (better protocol, accelerometer support, etc). 

Cheers,
Oren

eskofier, 2018-10-25:
Oren, in case you are too busy, we can build badges for fellow researchers. 
All, it would be important to know the demand for badges. 10, 100, 1000?

OrenLederman, 2018-10-25:
I actually haven't been keeping good track of the requests recently. Typically, people ask for some andges (about 10) to try out , and later on might need more. But making the badges by itself isn't too time consuming for me. Here are the problems I see:

* I can't sell badges since MIT is a non profit
* Ordering badges is about Ricky nowdays because of the shortage in capacitors. It requires fidning alternative capacitors every time and place the order quickly. 
* Badges then need to be tested and programmed
* And then, there's the initial support for using them and basic analysis :)

So by creating a community I'm hoping to made the information needed more available and help people help each other. Hopefully, in a way that scales.

patcon, 2018-10-25:
> Ordering badges is about Ricky nowdays because of the shortage in capacitors.

I _knew_ Ricky was behind it. He is admittedly a bit tricky.

patcon, 2018-10-25:
And @eskofier, might that offer apply to civic technologists who are working on citizen science initiatives? We are part of the [g0v.asia](https://g0v.asia) civic tech community (prounounced "gov-zero"), working loosely with [PDIS](https://pdis.nat.gov.tw/en/), part of the Taiwanese government.

We were looking to do a first run of 15. No pressure. (Email is patrick.c.connolly @ the googles)

OrenLederman, 2018-10-25:
Bah. That's what happens when I try to write quickly on my phone. I miss my
blackberry keyboard...

OrenLederman, 2018-10-25:
It's getting busy in here :-) . 
@patcon - another thing to consider is hosting a simple forums system somewhere to make it easier to ask questions and create discussions. Is this something that Seeed/PCBWay offer as part of their community projects?

patcon, 2018-10-25:
I've been investigating the seeed/pcbway systems for most of the afternoon, and it seems that they're pretty rudimentary. They offer comments and "likes", but no forums per se. I wouldn't want to try to manage a community over there -- just allow ordering and simple interactions. I'll think on other options. I might lean toward github (perhaps another repo) until that fails or gets complaints, just because that seems in flow with the other work flow?

PCBway actually seems better than seeed. PCBway allows you to share a project, and someone can add a PCB to the cart. There is a specific place on the project page to attach a BOM, and I think the idea is that you can then add another line item to the cart by asking for assembly. It's not seamless, but it's not bad.

Another option, though unsure how pricing would look: https://learn.sparkfun.com/tutorials/how-to-sell-your-widget-on-sparkfun#option-2-sparkfun-manufactures-you-get-a-royalty (perk of sparkfun is that they're fully assembled and have a high standard for docs and support)

OrenLederman, 2018-10-25:
I think that github is ok for tracking issues, but sometimes you just want to have a discussion, or ask questions. In particular, people ask me a lot of questions about tips for deployment and data analysis. Saving these questions in a forum instead of emails can be useful :) I'll try to look into that, and see where I can host something like that.

OrenLederman, 2018-10-26:
I'm not a huge fan of synchronous chat for large discussions. I think it's a good tool when you routinely work with other people and when you need to coordinate stuff (and we might need it sometimes).  

What I had in mind is more of a forum system. I'm thinking of the other use cases that I see, which is mostly Q&A and support - manufacturing/fabrication, questions about deployments (base stations and server) and data analysis. Creating topics will allow you to reduce clutter and make it easier to search (think stack overflow). 

I'm not sure what the solution is right now, I'll have to think about it for a bit.

OrenLederman, 2018-10-26:
Also, going back to one of the original questions here - does anyone have a preference for PCBWay or SeeedStudio? I can try and order a small batch of badges from one of them and see if the quality is ok

patcon, 2018-10-27:
PCBWay seems to have a better "project sharing" feature, so I was gearing to order from them. Thanks for asking!

Seeedstudio (as in, their project sharing feature) seems to be more for ppl coloring within the lines, building stuff from polished kits)

patcon, 2018-10-30:
Not ready for primetime yet, but I've set up stubs for project pages, so that others can see what it might look like to host on PCBWay:
https://www.pcbway.com/project/shareproject/Rhythm_Badge.html
https://www.pcbway.com/project/shareproject/Rhythm_Badge_Programmer.html?x=1

kasbah, 2018-10-30:
Hey, creator of Kitspace here. Obviously biased but some advantages I believe Kitspace has over other options:

- It's the only site that lets you purchase the parts required for self-assembly with a single click
- You can easily review part information in the BOM view
- Open source
- Not tied to any specific manufacturer or parts retailers (we currently link to specific ones but will keep adding to these)
- It's a front-end to your existing Git repository, if you change anything on Github it will be updated on Kitspace automatically

Full disclosure: I do currently earn and collect 10% commission on any order referred to PCBWay and Aisler. This has earned me about $70 in one year :slightly_smiling_face: . Once this hits some kind of workable threshold (where we can support the development of the site with it) we will look into passing this on to project creators.

If you are happy to put it up on Kitspace, I am happy to help you out with it. So let me know. Either way, this is a really interesting project. Do you think it could help people with [Prosopagnosia](https://en.wikipedia.org/wiki/Prosopagnosia)?

OrenLederman, 2018-10-30:
Thanks Kaspar (are you monitoring conversations about Kitspace? :)). I'll look into it more, but so far I see two issues:

1. When you place the order through Kitspace is only fills in the PCB info, but not the PCBA
2. A really cool feature that I'm missing is assigning a list of alternative parts. Especially now with the world shortage in capacitors.

kasbah, 2018-10-30:
Haha, no. @patcon @'ed me so I got a notification. 

1. Yes, it's only for PCB info for now. Extracting all the PCBA info and making sure it's correct is much harder. Does PCBWay offer this on their project sharing platform?
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

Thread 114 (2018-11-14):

HumanDynamics/openbadge #114: Rename project with consistent rhythm namespace

patcon, 2018-11-14:
Ok, so doing a quick inventory.

- random note: website is http://www.rhythm.mit.edu/rhythm-badges/

| Name | Proposed Name |
|---|---|
| `rhythm-server` | `rhythm-server-js` |
| `rhythm-rtc` | --- |
| `openbadge` | `rhythm-badge` |
| `openbadge-analysis` | `rhythm-badge-analysis` |
| `openbadge-hub-py` | `rhythm-hub-py` |
| `openbadge-hub` | `rhythm-hub-mobile` |
| `openbadge-analysis-examples` | `rhythm-badge-analysis-examples` |
| `openbadge-rfduino` | `rhythm-badge-rfduino` |
| `openbadge-server` | `rhythm-server-py` |
| `openbadge-analysis-test-badge` | `rhythm-badge-analysis-test-badge` |

I've still got some other summary I'm hoping to do, like getting active/inactive status, and which prices work together, but curious to hear more about how the ecosystem works :)

Once we have this sorted, I'm happy to put together some PRs to get the name change finalized and ready to go

OrenLederman, 2018-11-14:
Most of the current rhythm-* projects aren't mine, but i'll see if my colleague can change them. @dcalacci, what do you think? The names will make more sense if you use a more descriptive prefix for the online/web projects.

To maintain consistency, I prefer to have rhythm-badge-* for everything that is purely badge related. So:
openbadge-server -> rhythm-badge-server (no "py", since there's one server)
openbadge-hub-py -> rhythm-badge-hub-py
openbadge-hub -> rhythm-badge-hub-mobile

Note that the analysis package will be more difficult to change since it requires renaming the package itself and everything that points to that package (including many private analysis projects that I have). But it's doable. I'll try to allocate time for this sometimes soon.

patcon, 2018-11-14:
Ok sound good! Thanks! Might you or someone else be able to sketch on a scrap of paper the relations between the projects above, and post that here? Unless I'm missing something, it's hard to understand how they relate (both over time with deprecation, and within rhythm  ecosystem). The more detail on relationship, the better :)

OrenLederman, 2018-11-14:
Fair enough (and I should update the readme..). You should be able to see
some of it in this paper (might be behind a pay-wall) -
https://ieeexplore.ieee.org/stamp/stamp.jsp?arnumber=8259434

In general, these are the main repos:
openbadge <-> hub-py (or mobile) <-> server

People wear the badges. When turned on , the badges only broadcast their id
and wait to be activated by the system (by the hub). Once activated, they
collect and store data locally until the a hub request it). A unique case
of badge is a "beacon" - a badge we use only as a location beacon. These
badges simply broadcast their id. You can use ibeacons instead, but this
feature hasn't been tested that much, and not well documented. Also, when
you use a badge as a beacon, the system will configure it for you, keep
track of it's voltage, and make sure it's still active.

The hub gets the list of badges (and beacons) from the server, and
continuously look for badge and beacons. You can have multiple hubs (they
synchronize their work via the server). The hub will do a scan, then
connected to the badges it has been, one after the other. The hub will
activate badges that haven't been activated yet (for example, after
changing batteries), set their internal clock, and set the id and project
id that they broadcast (an optimization for how we track proximity). The
hub then request data from the badges, and store them locally. Every now
and then, the hub sends the data to the server.

The server contains the list of badges in each project, aggregates all the
data collected, and provide monitoring for the system's health (especially
with our new dashboard, yay!).

Besides that, there is the analysis library. You can use it to read our
JSON data format into python pandas, and then create the basic data
structures we use for analysis. The pipeline for proximity data is much
more mature and clean compared to the audio code. There are examples for
how to use them in the examples repo (which is currently messy, but it's
all there).

Hope this helps.

patcon, 2018-11-15:
This is so unbelievably helpful! Thanks Oren. I might try to synthesize it into a Google Drawing file that we could render in the README overview repo

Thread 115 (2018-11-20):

HumanDynamics/openbadge #115: Updating the image of the badge to newest version

bhimasta, 2018-11-20:
Hi @OrenLederman,

Since the last email that I sent to you, I have been able to order the badge through pcbway.com. It will take around one month for the entire process. The notes that organized by @patcon are becoming a huge help to this point.

In the past couple of days, I got some emails from them asking for several issues, such as whether they did the right things on soldering the switch. These questions were probably very easy questions for you.

2. What to do with the extra wielding points?
[image]

2. If this part is soldered correctly?
[image]

3. If this part is soldered correctly?
[image]

Honestly, I thought that giving them enough information such as the schematics, BOM, and centroid, everything will go smoothly. 

As I don't have any experience with this hardware engineering, so answering this questions is complicated for me. 

So the first things that I do as a beginner is to compare the picture of the rhythm badge that I order with the image of the rhythm badge showed in the readme.md, to see if the soldered in the right position and direction. 

However, It seems that the picture of the rhythm badge showed in the readme.md is different with a different position and different looks of the components. Is it the older version? If yes, perhaps, It would be better if you could update the image with the newest version, so people (like me), can easily validate our artifacts through visual.

Thank you very much.

OrenLederman, 2018-11-20:
I've been (very slowly..) looking at pcbway, but simply didn't have time to try and order from them myself :) . Looking at the files they request, they ask for the centroids, but I think that does not include the angle for each component. In most cases it's easy to tell, but not always.

In this case:
#2 - the extra welding points are for an alternative battery holder that we used to use in the past. Cheaper, but not as strong. It's ok to solder on top of it

#4 - both these components (microphone and switch) are fine

#3 - Based on what I see, I think it's ok. If the arrow is pointing at pin 1, then it's correct.

When you communicate with them, can you tell them that your colleagues (me) would like to make similar orders, and ask what would be the best way to provide the placement information? Also, ask them if there is something we can change in the files to make it easier for them.

I'll try to bring my high resolution camera to the office next and take an update photo

OrenLederman, 2018-11-20:
Ummm, at a closer look, I think they messed up some of the resistors - R3, R2, and R8 should be 1k resistors, but I think they placed 100k resistors (probably using the same ones they used for R5, R6, R7).

Can't tell if they messed up the capacitors as well (they aren't marked the same way resisters are).

bhimasta, 2018-11-20:
Yeah, they asked me about the centroid in the beginning and I (beginner) thought that the rotation column gives the info about the angle of each component. Is it not the case?

Sure, I will ask them on would be the best way to provide the placement information and other things that make it easier for them.

Oh, Thank you for also notice the resistor issue, I will also try to follow up this issue with them.

patcon, 2018-11-20:
This is awesome. Thanks for sharing @bhimasta :) moderate resolution photos of new badge versions would be really helpful when we're manually assembling ours (parts in transit now)

bhimasta, 2018-11-20:
@patcon, I would love to join your manually assembling sessions if you don't mind. :D

bhimasta, 2018-11-21:
@OrenLederman 

I just got the replied from them

> As for R2, R8, RC0603JR-071KL 1K- the silkscreen is 01B. If 100K, then silkscreen is 01D.
> So we think we have soldered R2 R8 correctly, what do you think?

> For efficient assembly, we would suggest you offer the following files:
> 1. Centroid file, see attached coordinate file for reference
> 2. Assembly Instruction Drawing - display the polarity of Diode, Audion, LED, pls use “+” ”-”; 
       display the orientation of IC, eg, dot for IC”s Pin1. 
       see attached components position file for reference

>3.3D map file-display the THT parts’location and orientation

>4. **Assembled real picture if you ever made, it will be the best reference.**

[Template_Components position file.pdf](https://github.com/HumanDynamics/openbadge/files/2602482/Template_Components.position.file.pdf)

OrenLederman, 2018-11-21:
>    1. *Assembled real picture if you ever made, it will be the best

I'll copy their recommendation to a new issue.
The resistors are ok. It was hard to see in the image, but indeed the
marking is 01B, with is +-1%, as opposed to the %5 I'm usually using (which
is perfectly fine)

OrenLederman, 2018-11-21:
Here's an temporary updated photo. I'll update the readme + place a copy with the gerber files after I process and clean it up 

[image]

bhimasta, 2018-11-22:
Thank you very much Oren!

closed 2019-01-22 by OrenLederman

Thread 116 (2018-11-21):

HumanDynamics/openbadge #116: [Support] Question from PCBWay on PCB manufacturing

patcon, 2018-11-21:
We've ordered programmer and badge boards from PCBWay. Programmer boards went off without a hitch. Badge boards had a quality assurance question:

> Ref attached screenshot, is it correctly designed as no hole is there for the pointed out pad ?

Attached: 
[image]

patcon, 2018-11-21:
In the meantime, I forwarded @bhimasta's image from the other thread, so hopefully that will answer question for them:
https://github.com/HumanDynamics/openbadge/issues/115#issue-382709017

bhimasta, 2018-11-21:
Considering we ordered to PCBWay using the same source of design, they didn't ask anything about this issue in my case. Is it weird, isn't it?

OrenLederman, 2018-11-21:
Patric - that is correct, no hole there. This large pad is part of the alternative battery holder we used to use in the past. Now the new battery holder is just soldered on top of it.

I kept the old design there as a backup since every change I make to the design triggers an order of another batch of prototypes and tests. It's quite common to have additional "stuff" in the hardware design that isn't used.

patcon, 2018-11-21:
Thanks Oren!

closed 2018-11-21 by patcon

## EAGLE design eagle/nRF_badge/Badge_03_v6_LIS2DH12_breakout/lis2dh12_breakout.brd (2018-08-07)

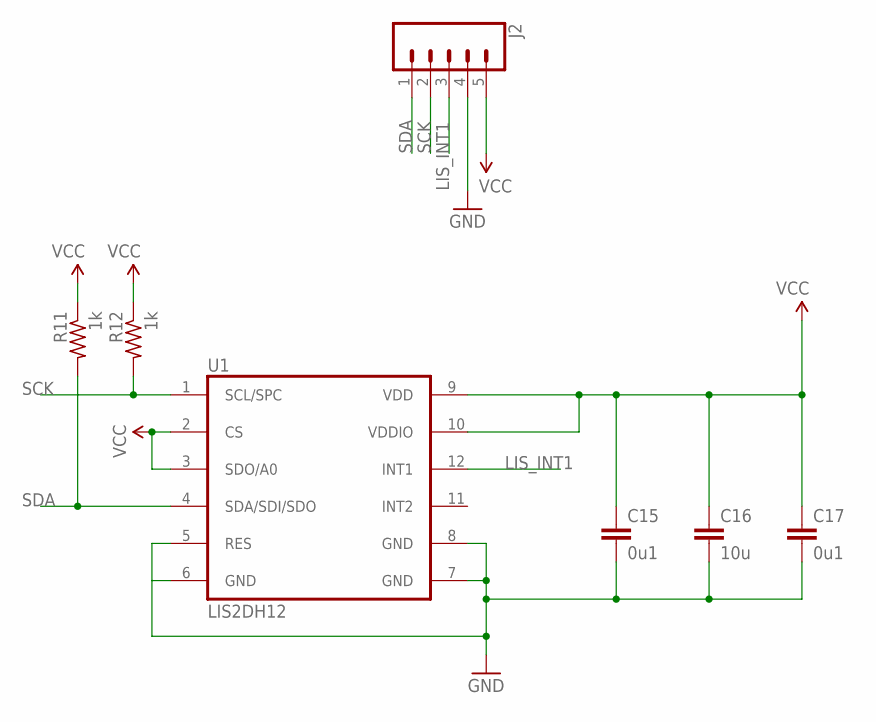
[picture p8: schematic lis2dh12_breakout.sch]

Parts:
C15, C17: 0u1; C0603
C16: 10u; C0603
J2: CONN_05NO_SILK; 1X05_NO_SILK
R11, R12: 1k; R0603
U1: LIS2DH12; LGA12

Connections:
GND: C15.2, C16.2, C17.2, J2.4, U1.5 (RES), U1.6 (GND), U1.7 (GND), U1.8 (GND)
LIS_INT1: J2.3, U1.12 (INT1)
SCK: J2.2, R12.2, U1.1 (SCL/SPC)
SDA: J2.1, R11.2, U1.4 (SDA/SDI/SDO)
VCC: C15.1, C16.1, C17.1, J2.5, R11.1, R12.1, U1.2 (CS), U1.3 (SDO/A0), U1.9 (VDD), U1.10 (VDDIO)

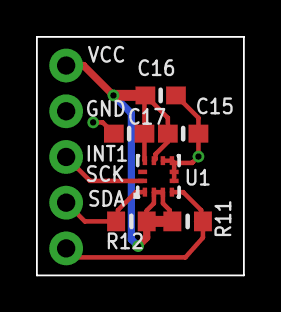
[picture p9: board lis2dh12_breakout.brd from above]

Board: 2 copper layers, 11.5 x 13.2 mm, 7 parts (0 on the bottom side), 5 nets.

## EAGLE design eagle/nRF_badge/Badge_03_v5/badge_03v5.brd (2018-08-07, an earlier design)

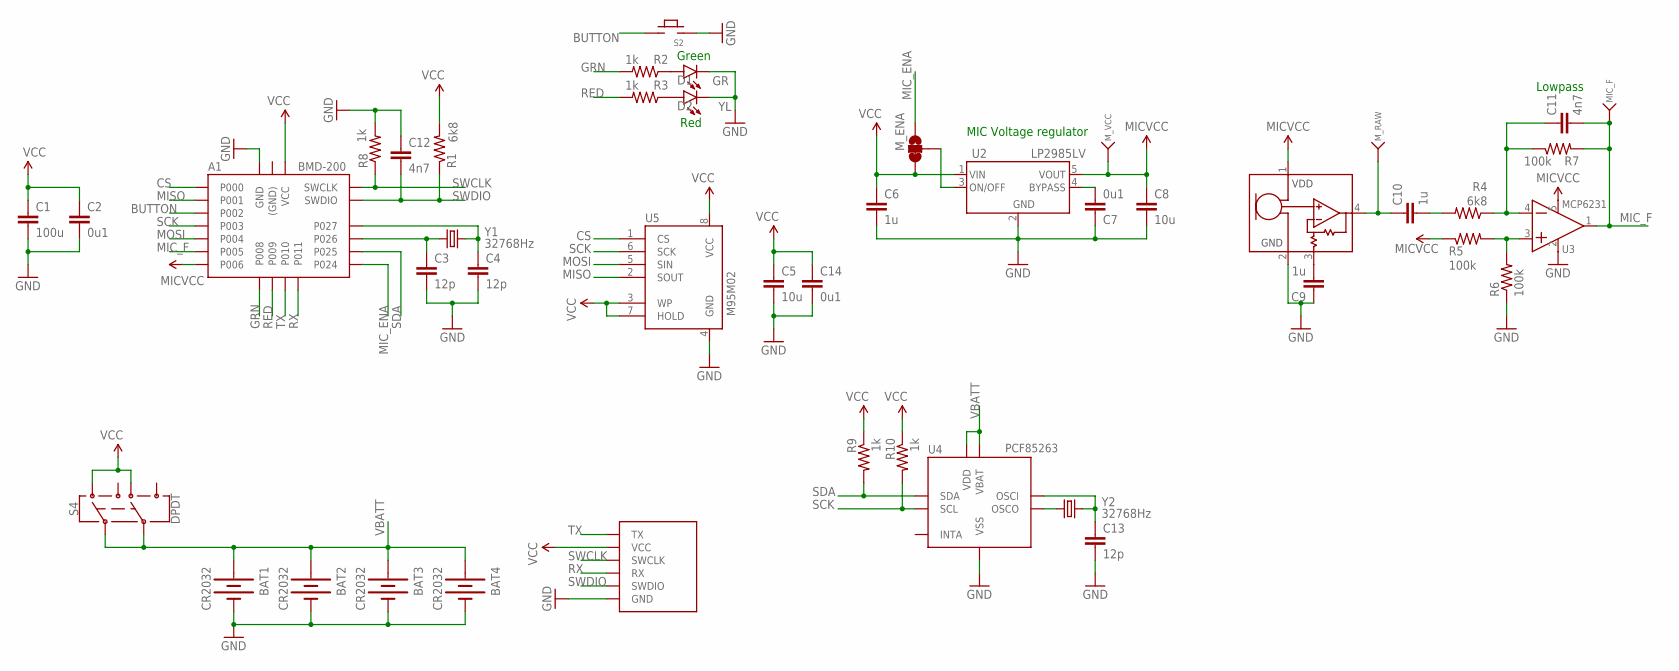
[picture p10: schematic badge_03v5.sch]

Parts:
A1: BMD-200
BAT1, BAT2: CR2032; BATTCON_20MM_4LEGS_ISO_NOCREAM
BAT3: CR2032; BU2032SM
BAT4: CR2032; BU2032SM_CREAM
C1: 100u; C1206
C2, C7, C14: 0u1; C0603
C3, C4, C13: 12p; C0603
C5, C8: 10u; C0603
C6, C9, C10: 1u; C0603
C11, C12: 4n7; C0603
D1: GR; LED-0603
D2: YL; LED-0603
J1: PROG_CONN_6; TH_CONN_6
MIC_F: TESTPOINT
MK1: SPU0414; MIC_SPU041X
M_ENA: JUMPER-PAD-3-2OF3_NC_BY_TRACE_SMALL; PAD-JUMPER-3-2OF3_NC_BY_TRACE_YES_SILK_FULL_BOX
M_RAW: TESTPOINT
M_VCC: TESTPOINT
R1, R4: 6k8; R0603
R2, R3, R8, R9, R10: 1k; R0603
R5, R6, R7: 100k; R0603
S2: TACT6mm; TACT1
S4: DPDT; SWITCH_DPDT_SMD_AYZ0202
U2: LP2985LV; SOT23-5L
U3: MCP6231; SOT23-5L
U4: PCF85263; SOIC8
U5: M95M02; SOIC8
Y1, Y2: 32768Hz; CRYSTAL_2SMD

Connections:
BUTTON: A1.P$13 (P002), S2.1, S2.2
CS: A1.P$11 (P000), U5.1 (CS)
GND: A1.P$1 (GND), A1.P$2 (GND), A1.P$3 (GND), A1.P$4 (GND), A1.P$7 (GND), A1.P$10 (GND), A1.P$19 (GND), A1.P$26 (GND), BAT1.NEG (-), BAT2.NEG (-), BAT3.-, BAT4.-, C1.2, C2.2, C3.2, C4.2, C5.2, C6.2, C7.1, C8.2, C9.1, C12.1, C13.2, C14.2, D1.C, D2.C, J1.GND, MK1.2 (GND), R6.1, R8.2, S2.3, S2.4, U2.2 (GND), U3.2 (GND), U4.4 (VSS), U5.4 (GND)
GRN: A1.P$20 (P008), R2.2
MICVCC: A1.P$17 (P006), C8.1, MK1.1 (VDD), M_VCC.P$1, R5.1, U2.5 (VOUT), U3.5 (VDD)
MIC_ENA: A1.P$5 (P024), M_ENA.1
MIC_F: A1.P$16 (P005), C11.2, MIC_F.P$1, R7.2, U3.1 (O)
MISO: A1.P$12 (P001), U5.2 (SOUT)
MOSI: A1.P$15 (P004), U5.5 (SIN)
unnamed: U4.2 (OSCO), Y2.P$2 (2)
unnamed: A1.P$8 (P026), C3.1, Y1.P$2 (2)
unnamed: D1.A, R2.1
unnamed: D2.A, R3.1
unnamed: C13.1, U4.1 (OSCI), Y2.P$1 (1)
unnamed: M_ENA.2, U2.3 (ON/OFF)
unnamed: C9.2, MK1.3 (GAIN)
unnamed: A1.P$9 (P027), C4.1, Y1.P$1 (1)
unnamed: C7.2, U2.4 (BYPASS)
unnamed: R5.2, R6.2, U3.3 (+)
unnamed: C10.1, MK1.4 (OUT), M_RAW.P$1
unnamed: C10.2, R4.2
unnamed: C11.1, R4.1, R7.1, U3.4 (-)
RED: A1.P$21 (P009), R3.2
RX: A1.P$23 (P011), J1.RX
SCK: A1.P$14 (P003), R10.2, U4.6 (SCL), U5.6 (SCK)
SDA: A1.P$6 (P025), R9.2, U4.5 (SDA)
SWCLK: A1.P$25 (SWCLK), J1.SWCLK, R8.1
SWDIO: A1.P$24 (SWDIO), C12.2, J1.SWDIO, R1.1
TX: A1.P$22 (P010), J1.TX
VBATT: BAT1.1 (+), BAT1.2 (+), BAT1.3 (+), BAT1.4 (+), BAT2.1 (+), BAT2.2 (+), BAT2.3 (+), BAT2.4 (+), BAT3.+, BAT4.+, S4.2, S4.5, U4.3 (VBAT), U4.8 (VDD)
VCC: A1.P$18 (VCC), C1.1, C2.1, C5.1, C6.1, C14.1, J1.VCC, M_ENA.3, R1.2, R9.1, R10.1, S4.1, S4.4, U2.1 (VIN), U5.3 (WP), U5.7 (HOLD), U5.8 (VCC)

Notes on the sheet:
Green
Red
MIC Voltage regulator
Lowpass

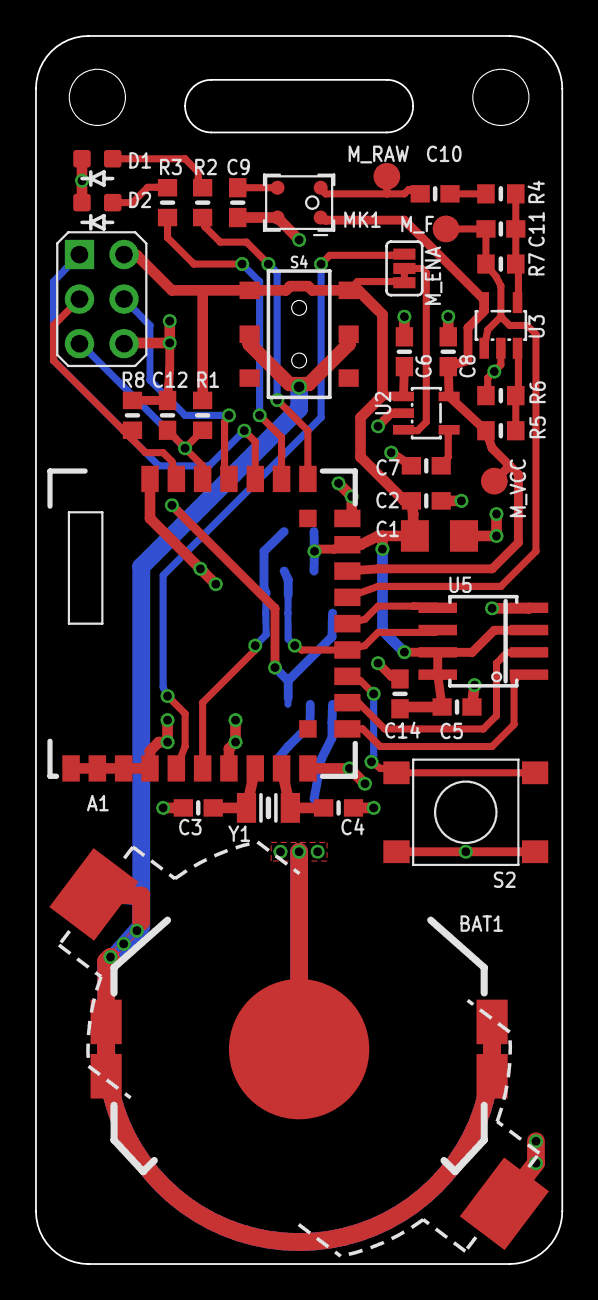
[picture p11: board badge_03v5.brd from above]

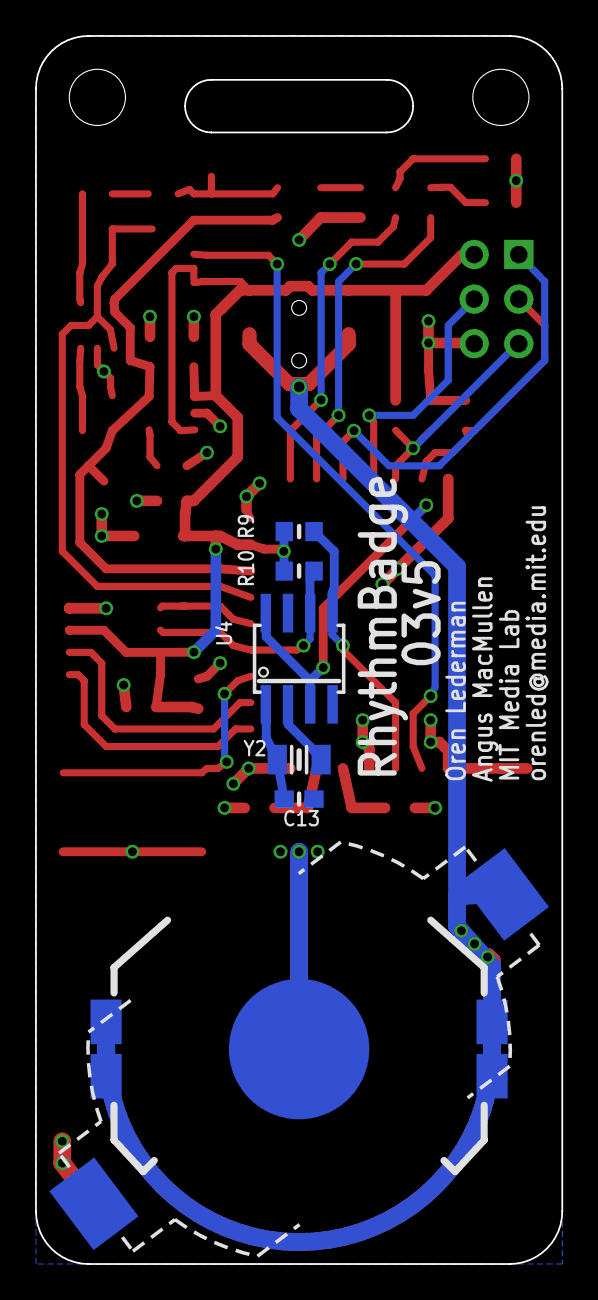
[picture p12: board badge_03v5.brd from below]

Board: 2 copper layers, 30.0 x 70.0 mm, 45 parts (7 on the bottom side), 31 nets.

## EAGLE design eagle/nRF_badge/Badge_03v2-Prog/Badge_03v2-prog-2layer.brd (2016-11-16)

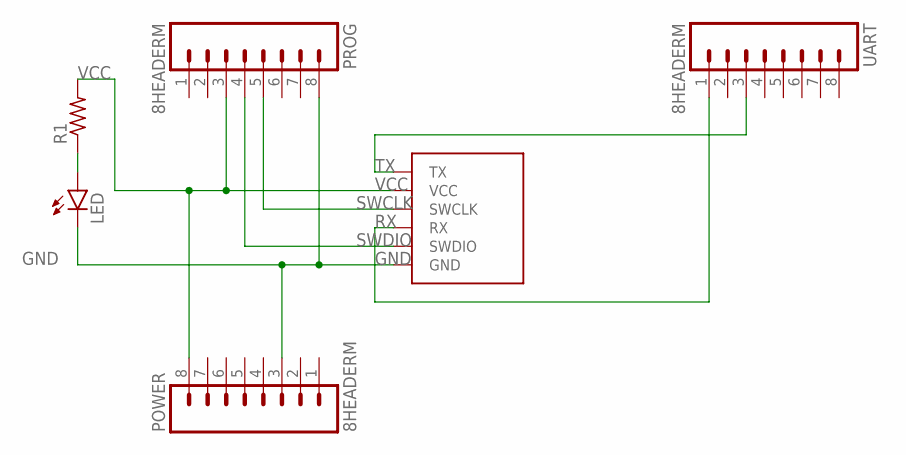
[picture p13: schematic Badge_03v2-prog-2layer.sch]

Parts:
J1: PROG_CONN_6; TH_CONN_6
LED: LED; LED-0603
POWER: 8HEADERM; 1X08_ROUND
PROG: 8HEADERM; 1X08_ROUND
R1: R-US_R0603; R0603
UART: 8HEADERM; 1X08_ROUND

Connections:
GND: J1.GND, LED.C, POWER.3, PROG.8
unnamed: LED.A, R1.1
RX: J1.RX, UART.1
SWCLK: J1.SWCLK, PROG.5
SWDIO: J1.SWDIO, PROG.4
TX: J1.TX, UART.3
VCC: J1.VCC, POWER.8, PROG.3, R1.2

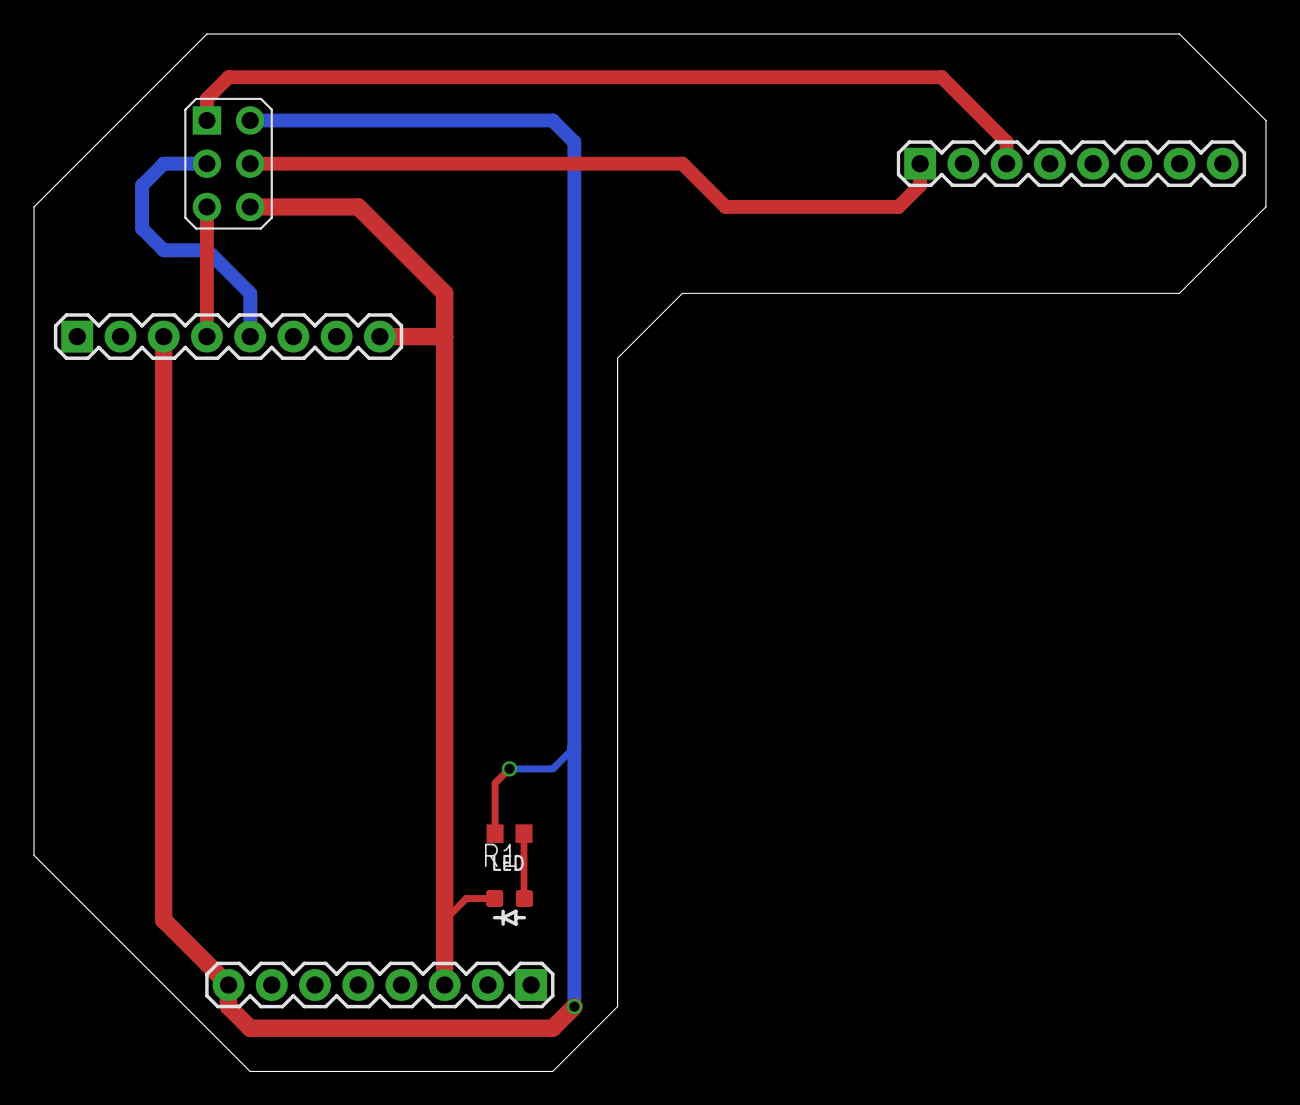
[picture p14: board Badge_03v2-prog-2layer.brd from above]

Board: 2 copper layers, 72.4 x 61.0 mm, 6 parts (0 on the bottom side), 7 nets.

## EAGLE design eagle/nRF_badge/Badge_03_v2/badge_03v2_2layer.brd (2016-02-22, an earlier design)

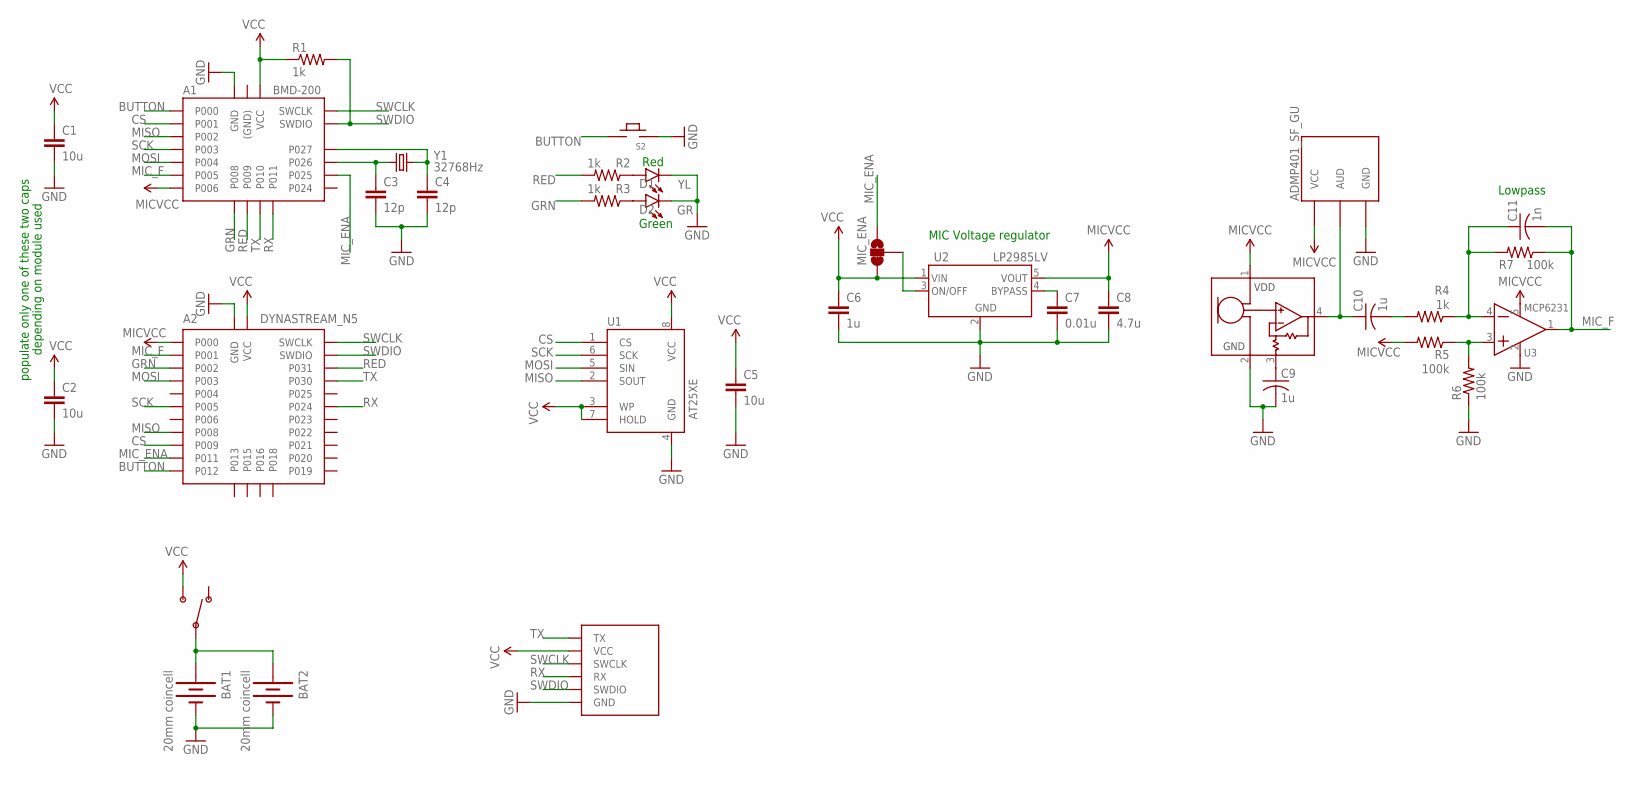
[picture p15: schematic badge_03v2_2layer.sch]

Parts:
A1: BMD-200
A2: DYNASTREAM_N5
A3: ADMP401_SF_GU; ADMP401_SF_SMD
BAT1: 20mm coincell; BATTCON_20MM_4LEGS_ISO
BAT2: 20mm coincell; BATTCON_20MM_4LEGS_ISO_NOCREAM
C1, C2, C5: 10u; C0603
C3, C4: 12p; C0603
C6, C9, C10: 1u; C0603
C7: 0.01u; C0603
C8: 4.7u; C0603
C11: 1n; C0603
D1: YL; LED-0603
D2: GR; LED-0603
J1: PROG_CONN_6; TH_CONN_6
MIC_ENA: DC/DC; PAD-JUMPER-3-2OF3_NC_BY_TRACE_YES_SILK_FULL_BOX
MK1: SPU0414(AMP); MIC_SPU041X
R1, R4: 1k; R0603
R2, R3: 1k; 0603-RES
R5, R6, R7: 100k; R0603
S1: CL-SB-12A-01
S2: TACT6MM4; TACT1
U1: AT25XE; SOIC8
U2: LP2985LV; SOT23-5L
U3: MCP6231; SOT23-5L
Y1: 32768Hz; CRYSTAL_2SMD

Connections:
BUTTON: A1.P$11 (P000), A2.D1 (P012), S2.1, S2.2
CS: A1.P$12 (P001), A2.E1 (P009), U1.1 (CS)
GND: A1.P$1 (GND), A1.P$2 (GND), A1.P$3 (GND), A1.P$4 (GND), A1.P$7 (GND), A1.P$10 (GND), A1.P$19 (GND), A1.P$26 (GND), A2.A2 (GND), A2.A3 (GND), A2.A4 (GND), A2.A5 (GND), A2.A6 (GND), A3.GND, A3.GNDT (GND), BAT1.NEG (-), BAT2.NEG (-), C1.2, C2.2, C3.2, C4.2, C5.2, C6.2, C7.2, C8.2, C9.2, D1.C, D2.C, J1.GND, MK1.2 (GND), R6.1, S2.3, S2.4, U1.4 (GND), U2.2 (GND), U3.2 (GND)
GRN: A1.P$20 (P008), A2.F5 (P002), R3.2
MICVCC: A1.P$17 (P006), A2.E5 (P000), A3.VCC, A3.VCCT (VCC), C8.1, MK1.1 (VDD), R5.2, U2.5 (VOUT), U3.5 (VDD)
MIC_ENA: A1.P$6 (P025), A2.E2 (P011), MIC_ENA.1
MIC_F: A1.P$16 (P005), A2.F4 (P001), C11.2, R7.1, U3.1 (O)
MISO: A1.P$13 (P002), A2.F1 (P008), U1.2 (SOUT)
MOSI: A1.P$15 (P004), A2.F3 (P003), U1.5 (SIN)
unnamed: A1.P$8 (P026), C3.1, Y1.P$2 (2)
unnamed: D1.A, R2.1
unnamed: D2.A, R3.1
unnamed: MIC_ENA.2, U2.3 (ON/OFF)
unnamed: C9.1, MK1.3 (GAIN)
unnamed: A1.P$9 (P027), C4.1, Y1.P$1 (1)
unnamed: C7.1, U2.4 (BYPASS)
unnamed: R5.1, R6.2, U3.3 (+)
unnamed: A3.AUD, A3.AUDT (AUD), C10.1, MK1.4 (OUT)
unnamed: C10.2, R4.2
unnamed: C11.1, R4.1, R7.2, U3.4 (-)
RED: A1.P$21 (P009), A2.F6 (P031), R2.2
RX: A1.P$23 (P011), A2.D6 (P024), J1.RX
SCK: A1.P$14 (P003), A2.F2 (P005), U1.6 (SCK)
SWCLK: A1.P$25 (SWCLK), A2.C1 (SWCLK), J1.SWCLK
SWDIO: A1.P$24 (SWDIO), A2.B1 (SWDIO), J1.SWDIO, R1.2
TX: A1.P$22 (P010), A2.E6 (P030), J1.TX
VBATT: BAT1.1 (+), BAT1.2 (+), BAT1.3 (+), BAT1.4 (+), BAT2.1 (+), BAT2.2 (+), BAT2.3 (+), BAT2.4 (+), S1.C
VCC: A1.P$18 (VCC), A2.B5 (VCC), A2.B6 (VCC), A2.C5 (VCC), A2.C6 (VCC), C1.1, C2.1, C5.1, C6.1, J1.VCC, MIC_ENA.3, R1.1, S1.2, U1.3 (WP), U1.7 (HOLD), U1.8 (VCC), U2.1 (VIN)

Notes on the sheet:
Green
Red
MIC Voltage regulator
Lowpass
populate only one of these two caps
depending on module used

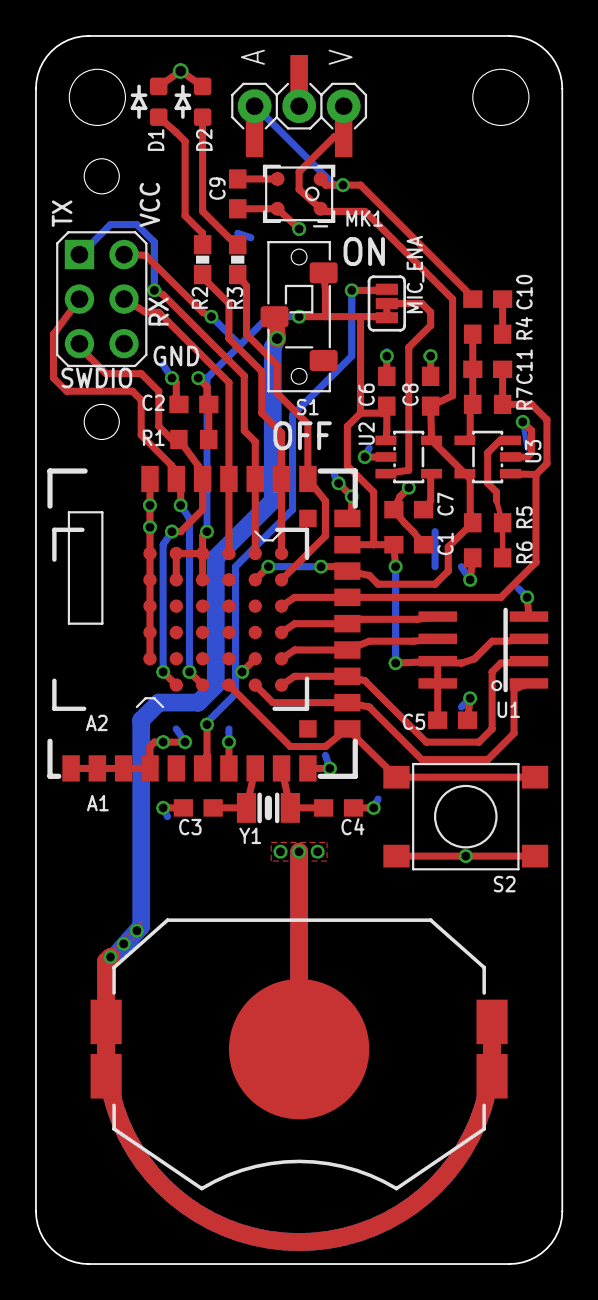
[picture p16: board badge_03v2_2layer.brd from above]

Board: 2 copper layers, 30.0 x 70.0 mm, 34 parts (1 on the bottom side), 28 nets.

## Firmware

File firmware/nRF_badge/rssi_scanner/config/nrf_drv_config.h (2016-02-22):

/* Copyright (c) 2015 Nordic Semiconductor. All Rights Reserved.
 *
 * The information contained herein is property of Nordic Semiconductor ASA.
 * Terms and conditions of usage are described in detail in NORDIC
 * SEMICONDUCTOR STANDARD SOFTWARE LICENSE AGREEMENT.
 *
 * Licensees are granted free, non-transferable use of the information. NO
 * WARRANTY of ANY KIND is provided. This heading must NOT be removed from
 * the file.
 *
 */

#ifndef NRF_DRV_CONFIG_H
#define NRF_DRV_CONFIG_H

/* CLOCK */
#define CLOCK_CONFIG_XTAL_FREQ          NRF_CLOCK_XTALFREQ_16MHz
#define CLOCK_CONFIG_LF_SRC             NRF_CLOCK_LF_SRC_Xtal
#define CLOCK_CONFIG_LF_RC_CAL_INTERVAL RC_2000MS_CALIBRATION_INTERVAL
#define CLOCK_CONFIG_IRQ_PRIORITY       APP_IRQ_PRIORITY_LOW

/* GPIOTE */
#define GPIOTE_ENABLED 1

#if (GPIOTE_ENABLED == 1)
#define GPIOTE_CONFIG_USE_SWI_EGU false
#define GPIOTE_CONFIG_IRQ_PRIORITY APP_IRQ_PRIORITY_HIGH
#define GPIOTE_CONFIG_NUM_OF_LOW_POWER_EVENTS 5
#endif

/* TIMER */
#define TIMER0_ENABLED 0

#if (TIMER0_ENABLED == 1)
#define TIMER0_CONFIG_FREQUENCY    NRF_TIMER_FREQ_16MHz
#define TIMER0_CONFIG_MODE         TIMER_MODE_MODE_Timer
#define TIMER0_CONFIG_BIT_WIDTH    TIMER_BITMODE_BITMODE_32Bit
#define TIMER0_CONFIG_IRQ_PRIORITY APP_IRQ_PRIORITY_LOW

#define TIMER0_INSTANCE_INDEX      0
#endif

#define TIMER1_ENABLED 0

#if (TIMER1_ENABLED == 1)
#define TIMER1_CONFIG_FREQUENCY    NRF_TIMER_FREQ_16MHz
#define TIMER1_CONFIG_MODE         TIMER_MODE_MODE_Timer
#define TIMER1_CONFIG_BIT_WIDTH    TIMER_BITMODE_BITMODE_16Bit
#define TIMER1_CONFIG_IRQ_PRIORITY APP_IRQ_PRIORITY_LOW

#define TIMER1_INSTANCE_INDEX      (TIMER0_ENABLED)
#endif
 
#define TIMER2_ENABLED 0

#if (TIMER2_ENABLED == 1)
#define TIMER2_CONFIG_FREQUENCY    NRF_TIMER_FREQ_16MHz
#define TIMER2_CONFIG_MODE         TIMER_MODE_MODE_Timer
#define TIMER2_CONFIG_BIT_WIDTH    TIMER_BITMODE_BITMODE_16Bit
#define TIMER2_CONFIG_IRQ_PRIORITY APP_IRQ_PRIORITY_LOW

#define TIMER2_INSTANCE_INDEX      (TIMER1_ENABLED+TIMER0_ENABLED)
#endif
 
#define TIMER_COUNT (TIMER0_ENABLED + TIMER1_ENABLED + TIMER2_ENABLED)

/* RTC */
#define RTC0_ENABLED 0

#if (RTC0_ENABLED == 1)
#define RTC0_CONFIG_FREQUENCY    32678
#define RTC0_CONFIG_IRQ_PRIORITY APP_IRQ_PRIORITY_LOW
#define RTC0_CONFIG_RELIABLE     false

#define RTC0_INSTANCE_INDEX      0
#endif

#define RTC1_ENABLED 1

#if (RTC1_ENABLED == 1)
#define RTC1_CONFIG_FREQUENCY    32768
#define RTC1_CONFIG_IRQ_PRIORITY APP_IRQ_PRIORITY_LOW
#define RTC1_CONFIG_RELIABLE     false

#define RTC1_INSTANCE_INDEX      (RTC0_ENABLED)
#endif

#define RTC_COUNT                (RTC0_ENABLED+RTC1_ENABLED)

#define NRF_MAXIMUM_LATENCY_US 2000

/* RNG */
#define RNG_ENABLED 0

#if (RNG_ENABLED == 1)
#define RNG_CONFIG_ERROR_CORRECTION true
#define RNG_CONFIG_POOL_SIZE        8
#define RNG_CONFIG_IRQ_PRIORITY     APP_IRQ_PRIORITY_LOW
#endif


/* QDEC */
#define QDEC_ENABLED 0

#if (QDEC_ENABLED == 1)
#define QDEC_CONFIG_REPORTPER    NRF_QDEC_REPORTPER_10
#define QDEC_CONFIG_SAMPLEPER    NRF_QDEC_SAMPLEPER_16384us
#define QDEC_CONFIG_PIO_A        1
#define QDEC_CONFIG_PIO_B        2
#define QDEC_CONFIG_PIO_LED      3
#define QDEC_CONFIG_LEDPRE       511
#define QDEC_CONFIG_LEDPOL       NRF_QDEC_LEPOL_ACTIVE_HIGH
#define QDEC_CONFIG_IRQ_PRIORITY APP_IRQ_PRIORITY_LOW
#define QDEC_CONFIG_DBFEN        false
#define QDEC_CONFIG_SAMPLE_INTEN false
#endif

/* LPCOMP */
#define LPCOMP_ENABLED 0

#if (LPCOMP_ENABLED == 1)
#define LPCOMP_CONFIG_REFERENCE    NRF_LPCOMP_REF_SUPPLY_FOUR_EIGHT
#define LPCOMP_CONFIG_DETECTION    NRF_LPCOMP_DETECT_DOWN
#define LPCOMP_CONFIG_IRQ_PRIORITY APP_IRQ_PRIORITY_LOW
#define LPCOMP_CONFIG_INPUT        NRF_LPCOMP_INPUT_0
#endif

/* WDT */
#define WDT_ENABLED 0

#if (WDT_ENABLED == 1)
#define WDT_CONFIG_BEHAVIOUR     NRF_WDT_BEHAVIOUR_RUN_SLEEP
#define WDT_CONFIG_RELOAD_VALUE  2000
#define WDT_CONFIG_IRQ_PRIORITY  APP_IRQ_PRIORITY_HIGH
#endif

#endif // NRF_DRV_CONFIG_H

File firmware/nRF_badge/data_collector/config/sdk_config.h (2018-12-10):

#ifndef SDK_CONFIG_H
#define SDK_CONFIG_H
// <<< Use Configuration Wizard in Context Menu >>>\n
#ifdef USE_APP_CONFIG
#include "app_config.h"
#endif
// <h> nRF_Drivers 



//#include <nrf_peripherals.h> is included in every peripheral module, so don't need to include it here!
//#include <nrf51822_peripherals.h>


// APP FIFO ENABLED
#ifndef APP_FIFO_ENABLED
#define APP_FIFO_ENABLED 1
#endif



// <h> nRF_BLE 

//==========================================================
// <q> BLE_ADVERTISING_ENABLED  - ble_advertising - Advertising module
 

#ifndef BLE_ADVERTISING_ENABLED
#define BLE_ADVERTISING_ENABLED 1
#endif

// </h> 
//==========================================================



// <h> nRF_BLE_Services 

//==========================================================
// <q> BLE_NUS_ENABLED  - ble_nus - Nordic UART Service
 

#ifndef BLE_NUS_ENABLED
#define BLE_NUS_ENABLED 1
#endif

// </h> 
//==========================================================


//==========================================================
// <e> ADC_ENABLED - nrf_drv_adc - Driver for ADC peripheral (nRF51)
//==========================================================
#ifndef ADC_ENABLED
#define ADC_ENABLED 1
#endif
#if  ADC_ENABLED
// <o> ADC_CONFIG_IRQ_PRIORITY  - Interrupt priority
 

// <i> Priorities 0,2 (nRF51) and 0,1,4,5 (nRF52) are reserved for SoftDevice
// <0=> 0 (highest) 
// <1=> 1 
// <2=> 2 
// <3=> 3 

#ifndef ADC_CONFIG_IRQ_PRIORITY
#define ADC_CONFIG_IRQ_PRIORITY 3
#endif

// <e> ADC_CONFIG_LOG_ENABLED - Enables logging in the module.
//==========================================================
#ifndef ADC_CONFIG_LOG_ENABLED
#define ADC_CONFIG_LOG_ENABLED 0
#endif
#if  ADC_CONFIG_LOG_ENABLED
// <o> ADC_CONFIG_LOG_LEVEL  - Default Severity level
 
// <0=> Off 
// <1=> Error 
// <2=> Warning 
// <3=> Info 
// <4=> Debug 

#ifndef ADC_CONFIG_LOG_LEVEL
#define ADC_CONFIG_LOG_LEVEL 3
#endif

// <o> ADC_CONFIG_INFO_COLOR  - ANSI escape code prefix.
 
// <0=> Default 
// <1=> Black 
// <2=> Red 
// <3=> Green 
// <4=> Yellow 
// <5=> Blue 
// <6=> Magenta 
// <7=> Cyan 
// <8=> White 

#ifndef ADC_CONFIG_INFO_COLOR
#define ADC_CONFIG_INFO_COLOR 0
#endif

// <o> ADC_CONFIG_DEBUG_COLOR  - ANSI escape code prefix.
 
// <0=> Default 
// <1=> Black 
// <2=> Red 
// <3=> Green 
// <4=> Yellow 
// <5=> Blue 
// <6=> Magenta 
// <7=> Cyan 
// <8=> White 

#ifndef ADC_CONFIG_DEBUG_COLOR
#define ADC_CONFIG_DEBUG_COLOR 0
#endif

#endif //ADC_CONFIG_LOG_ENABLED
// </e>

#endif //ADC_ENABLED
// </e>


//==========================================================
// <e> APP_TIMER_ENABLED - app_timer - Application timer functionality
//==========================================================
#ifndef APP_TIMER_ENABLED
#define APP_TIMER_ENABLED 1
#endif
#if  APP_TIMER_ENABLED
// <q> APP_TIMER_WITH_PROFILER  - Enable app_timer profiling
 

#ifndef APP_TIMER_WITH_PROFILER
#define APP_TIMER_WITH_PROFILER 0
#endif

// <q> APP_TIMER_KEEPS_RTC_ACTIVE  - Enable RTC always on
 

// <i> If option is enabled RTC is kept running even if there is no active timers.
// <i> This option can be used when app_timer is used for timestamping.

#ifndef APP_TIMER_KEEPS_RTC_ACTIVE
#define APP_TIMER_KEEPS_RTC_ACTIVE 0
#endif

#endif //APP_TIMER_ENABLED
// </e>


//==========================================================
// <e> APP_SCHEDULER_ENABLED - app_scheduler - Application scheduler functionality
//==========================================================
#ifndef APP_SCHEDULER_ENABLED
#define APP_SCHEDULER_ENABLED 1
#endif //APP_SCHEDULER_ENABLED
// </e>


//==========================================================
// <e> CLOCK_ENABLED - nrf_drv_clock - CLOCK peripheral driver
//==========================================================
#ifndef CLOCK_ENABLED
#define CLOCK_ENABLED 1
#endif
#if  CLOCK_ENABLED
// <o> CLOCK_CONFIG_XTAL_FREQ  - HF XTAL Frequency
 
// <0=> Default (64 MHz) 
// <255=> Default (16 MHz) 
// <0=> 32 MHz 

#ifndef CLOCK_CONFIG_XTAL_FREQ
#define CLOCK_CONFIG_XTAL_FREQ 255
#endif

// <o> CLOCK_CONFIG_LF_SRC  - LF Clock Source
 
// <0=> RC 
// <1=> XTAL 
// <2=> Synth 

#ifndef CLOCK_CONFIG_LF_SRC
#define CLOCK_CONFIG_LF_SRC 1
#endif

// <o> CLOCK_CONFIG_IRQ_PRIORITY  - Interrupt priority
 

// <i> Priorities 0,2 (nRF51) and 0,1,4,5 (nRF52) are reserved for SoftDevice
// <0=> 0 (highest) 
// <1=> 1 
// <2=> 2 
// <3=> 3 

#ifndef CLOCK_CONFIG_IRQ_PRIORITY
#define CLOCK_CONFIG_IRQ_PRIORITY 3
#endif

// <e> CLOCK_CONFIG_LOG_ENABLED - Enables logging in the module.
//==========================================================
#ifndef CLOCK_CONFIG_LOG_ENABLED
#define CLOCK_CONFIG_LOG_ENABLED 0
#endif
#if  CLOCK_CONFIG_LOG_ENABLED
// <o> CLOCK_CONFIG_LOG_LEVEL  - Default Severity level
 
// <0=> Off 
// <1=> Error 
// <2=> Warning 
// <3=> Info 
// <4=> Debug 

#ifndef CLOCK_CONFIG_LOG_LEVEL
#define CLOCK_CONFIG_LOG_LEVEL 3
#endif

// <o> CLOCK_CONFIG_INFO_COLOR  - ANSI escape code prefix.
 
// <0=> Default 
// <1=> Black 
// <2=> Red 
// <3=> Green 
// <4=> Yellow 
// <5=> Blue 
// <6=> Magenta 
// <7=> Cyan 
// <8=> White 

#ifndef CLOCK_CONFIG_INFO_COLOR
#define CLOCK_CONFIG_INFO_COLOR 0
#endif

// <o> CLOCK_CONFIG_DEBUG_COLOR  - ANSI escape code prefix.
 
// <0=> Default 
// <1=> Black 
// <2=> Red 
// <3=> Green 
// <4=> Yellow 
// <5=> Blue 
// <6=> Magenta 
// <7=> Cyan 
// <8=> White 

#ifndef CLOCK_CONFIG_DEBUG_COLOR
#define CLOCK_CONFIG_DEBUG_COLOR 0
#endif

#endif //CLOCK_CONFIG_LOG_ENABLED
// </e>

#endif //CLOCK_ENABLED
// </e>



// <e> FSTORAGE_ENABLED - fstorage - Flash storage module
//==========================================================
#ifndef FSTORAGE_ENABLED
#define FSTORAGE_ENABLED 1
#endif
#if  FSTORAGE_ENABLED
// <o> FS_QUEUE_SIZE - Configures the size of the internal queue. 
// <i> Increase this if there are many users, or if it is likely that many
// <i> operation will be queued at once without waiting for the previous operations
// <i> to complete. In general, increase the queue size if you frequently receive
// <i> @ref FS_ERR_QUEUE_FULL errors when calling @ref fs_store or @ref fs_erase.

#ifndef FS_QUEUE_SIZE
#define FS_QUEUE_SIZE 4
#endif

// <o> FS_OP_MAX_RETRIES - Number attempts to execute an operation if the SoftDevice fails. 
// <i> Increase this value if events return the @ref FS_ERR_OPERATION_TIMEOUT
// <i> error often. The SoftDevice may fail to schedule flash access due to high BLE activity.

#ifndef FS_OP_MAX_RETRIES
#define FS_OP_MAX_RETRIES 5
#endif

// <o> FS_MAX_WRITE_SIZE_WORDS - Maximum number of words to be written to flash in a single operation. 
// <i> Tweaking this value can increase the chances of the SoftDevice being
// <i> able to fit flash operations in between radio activity. This value is bound by the
// <i> maximum number of words which the SoftDevice can write to flash in a single call to
// <i> @ref sd_flash_write, which is 256 words for nRF51 ICs and 1024 words for nRF52 ICs.

#ifndef FS_MAX_WRITE_SIZE_WORDS
#define FS_MAX_WRITE_SIZE_WORDS 256
#endif



#endif //FSTORAGE_ENABLED
// </e>

//==========================================================
// <e> GPIOTE_ENABLED - nrf_drv_gpiote - GPIOTE peripheral driver
//==========================================================
#ifndef GPIOTE_ENABLED
#define GPIOTE_ENABLED 1
#endif
#if  GPIOTE_ENABLED
// <o> GPIOTE_CONFIG_NUM_OF_LOW_POWER_EVENTS - Number of lower power input pins 
#ifndef GPIOTE_CONFIG_NUM_OF_LOW_POWER_EVENTS
#define GPIOTE_CONFIG_NUM_OF_LOW_POWER_EVENTS 5 //1 
#endif

// <o> GPIOTE_CONFIG_IRQ_PRIORITY  - Interrupt priority
 

// <i> Priorities 0,2 (nRF51) and 0,1,4,5 (nRF52) are reserved for SoftDevice
// <0=> 0 (highest) 
// <1=> 1 
// <2=> 2 
// <3=> 3 

#ifndef GPIOTE_CONFIG_IRQ_PRIORITY
#define GPIOTE_CONFIG_IRQ_PRIORITY 1 // 3
#endif

// <e> GPIOTE_CONFIG_LOG_ENABLED - Enables logging in the module.
//==========================================================
#ifndef GPIOTE_CONFIG_LOG_ENABLED
#define GPIOTE_CONFIG_LOG_ENABLED 0
#endif
#if  GPIOTE_CONFIG_LOG_ENABLED
// <o> GPIOTE_CONFIG_LOG_LEVEL  - Default Severity level
 
// <0=> Off 
// <1=> Error 
// <2=> Warning 
// <3=> Info 
// <4=> Debug 

#ifndef GPIOTE_CONFIG_LOG_LEVEL
#define GPIOTE_CONFIG_LOG_LEVEL 3
#endif

// <o> GPIOTE_CONFIG_INFO_COLOR  - ANSI escape code prefix.
 
// <0=> Default 
// <1=> Black 
// <2=> Red 
// <3=> Green 
// <4=> Yellow 
// <5=> Blue 
// <6=> Magenta 
// <7=> Cyan 
// <8=> White 

#ifndef GPIOTE_CONFIG_INFO_COLOR
#define GPIOTE_CONFIG_INFO_COLOR 0
#endif

// <o> GPIOTE_CONFIG_DEBUG_COLOR  - ANSI escape code prefix.
 
// <0=> Default 
// <1=> Black 
// <2=> Red 
// <3=> Green 
// <4=> Yellow 
// <5=> Blue 
// <6=> Magenta 
// <7=> Cyan 
// <8=> White 

#ifndef GPIOTE_CONFIG_DEBUG_COLOR
#define GPIOTE_CONFIG_DEBUG_COLOR 0
#endif

#endif //GPIOTE_CONFIG_LOG_ENABLED
// </e>

#endif //GPIOTE_ENABLED
// </e>

//==========================================================
// <e> LPCOMP_ENABLED - nrf_drv_lpcomp - LPCOMP peripheral driver
//==========================================================
#ifndef LPCOMP_ENABLED
#define LPCOMP_ENABLED 0
#endif
#if  LPCOMP_ENABLED
// <o> LPCOMP_CONFIG_REFERENCE  - Reference voltage
 
// <0=> Supply 1/8 
// <1=> Supply 2/8 
// <2=> Supply 3/8 
// <3=> Supply 4/8 
// <4=> Supply 5/8 
// <5=> Supply 6/8 
// <6=> Supply 7/8 
// <8=> Supply 1/16 (nRF52) 
// <9=> Supply 3/16 (nRF52) 
// <10=> Supply 5/16 (nRF52) 
// <11=> Supply 7/16 (nRF52) 
// <12=> Supply 9/16 (nRF52) 
// <13=> Supply 11/16 (nRF52) 
// <14=> Supply 13/16 (nRF52) 
// <15=> Supply 15/16 (nRF52) 
// <7=> External Ref 0 
// <65543=> External Ref 1 

#ifndef LPCOMP_CONFIG_REFERENCE
#define LPCOMP_CONFIG_REFERENCE 3
#endif

// <o> LPCOMP_CONFIG_DETECTION  - Detection
 
// <0=> Crossing 
// <1=> Up 
// <2=> Down 

#ifndef LPCOMP_CONFIG_DETECTION
#define LPCOMP_CONFIG_DETECTION 2
#endif

// <o> LPCOMP_CONFIG_INPUT  - Analog input
 
// <0=> 0 
// <1=> 1 
// <2=> 2 
// <3=> 3 
// <4=> 4 
// <5=> 5 
// <6=> 6 
// <7=> 7 

#ifndef LPCOMP_CONFIG_INPUT
#define LPCOMP_CONFIG_INPUT 0
#endif

// <q> LPCOMP_CONFIG_HYST  - Hysteresis
 

#ifndef LPCOMP_CONFIG_HYST
#define LPCOMP_CONFIG_HYST 0
#endif

// <o> LPCOMP_CONFIG_IRQ_PRIORITY  - Interrupt priority
 

// <i> Priorities 0,2 (nRF51) and 0,1,4,5 (nRF52) are reserved for SoftDevice
// <0=> 0 (highest) 
// <1=> 1 
// <2=> 2 
// <3=> 3 

#ifndef LPCOMP_CONFIG_IRQ_PRIORITY
#define LPCOMP_CONFIG_IRQ_PRIORITY 3
#endif

// <e> LPCOMP_CONFIG_LOG_ENABLED - Enables logging in the module.
//==========================================================
#ifndef LPCOMP_CONFIG_LOG_ENABLED
#define LPCOMP_CONFIG_LOG_ENABLED 0
#endif
#if  LPCOMP_CONFIG_LOG_ENABLED
// <o> LPCOMP_CONFIG_LOG_LEVEL  - Default Severity level
 
// <0=> Off 
// <1=> Error 
// <2=> Warning 
// <3=> Info 
// <4=> Debug 

#ifndef LPCOMP_CONFIG_LOG_LEVEL
#define LPCOMP_CONFIG_LOG_LEVEL 3
#endif

// <o> LPCOMP_CONFIG_INFO_COLOR  - ANSI escape code prefix.
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

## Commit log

2016-02-22 Add badge hardware/firmware files, nRF server files. Gitignore eagle backup files, _build folder.
    [Badge_03v2-prog-schem.brd, Badge_03v2-prog-schem.sch, badge_03v2_2layer.brd, badge_03v2_2layer.sch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]
2016-02-28 add mic samples adn threshold. Not finazlied yes
2016-02-28 added printouts
2016-03-08 adding code for streaming samples (instead of storing them)
2016-03-10 sometimes doesn't disconnect properly. added a nested onConnect error handling that saves the deviceId
2016-03-14 Badge 03v4 hardware design Changes include: Reduce lowpass cutoff to ~340Hz, increase gain to ~15x Switched to EEPROM storage Added i2c RTC Added bypass cap to SWDIO, reduce SWDIO pullup strength Add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
    [badge_03v4.brd, badge_03v4.sch]
2016-03-15 Added ULPs to generate BOM and centroid data; post-processed BOM with Digikey part #'s
    [badge_03v4.brd, badge_03v4.sch, badge_03v4_bom.csv, badge_03v4_centroid.csv]
2016-03-15 Fixed some silkscreen sizes. Added CAM job. Exported badge 03v4 with RTC.
    [badge_03v4.GBL, badge_03v4.GBO, badge_03v4.GBP, badge_03v4.GBS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]
2016-03-16 Badge turns on LED when connected (good for testing). Various changes to app
2016-03-18 getting the device id from peripheral
2016-03-19 Disable scanning by default. (currently no method to re-enable at runtime)
2016-03-20 added a watchdog interval that keeps an eye for timeouts and connects to devices every several seconds
2016-04-09 Milliseconds are now added to timestamps. Milliseconds are written to data files
2016-04-10 Now saving samples in sqlite. Data are saved in csv as well, for backward compatibility
2016-04-17 Move MIC_PIN/MIC_AREF definitions to [board].h files. Add these definitions for badge_03v4.
2016-04-20 started building up the UI to work as specified there's a settings page (as well as a framework for pages) that you can use to save your group id the main page pulls the group's info from firebase an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
2016-04-24 Fixed status request + receiving to match current protocol.
2016-04-29 manually fixing BOM in badge file
    [badge_03v4.GBL, badge_03v4.GBO, badge_03v4.GBP, badge_03v4.GBS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]
2016-04-29 Fixed Eagle files and re-exported gerbers.
    [badge_03v4.GTO, badge_03v4.brd, badge_03v4.sch]
2016-04-29 more minor changes, and a script for combining centroids and bom
    [badge_03v4_bom.csv]
2016-05-02 Centroids were misaligned with gerber files. Following Jonathan's advice: Try checking/unchecking Pos. Coord. in your CAM job in Eagle, re-generate your Pick and Place, and see if that changes anythi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
    [badge_03v4.GBL, badge_03v4.GBO, badge_03v4.GBP, badge_03v4.GBS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]
2016-05-02 Setting programmer to use lower speed in order to handle the capacitor on SWDIO
2016-05-11 modified how timeouts work, so they handle a badge running out of battery or breaking
2016-05-13 Setting up env for python code in DataAnalyzer. Implemented an adjusting threshold for samples
2016-05-17 app now updates the threshold and cutoff based on sample mean .small fix in calling dateToString
2016-05-18 basic code for comparing samples from multiple badges
2016-05-19 Changed dates to milliseconds (instead of Date). fixed some issues with comparison of volumes.
2016-05-19 only sync the logs for the current group
2016-05-23 Badge programmer, 2 layers version
    [Badge_03v2-prog-2layer.brd, Badge_03v2-prog-2layer.sch]
2016-05-23 fixed up the readme minor style things added a script to run it only if a phone is attached
2016-05-25 Server receives chunk number of samples.
2016-05-27 Removed deprecated material from main.c
2016-05-30 Added code for checking gaps in the data. Add code for comparing battery usage
2016-05-30 Comparing battery usage with the new firmware
2016-05-30 Fix SCK idle state (no power draw when idle)
2016-05-31 Read battery when radio inactive. Pause advertising after disconnect, if requested.
2016-06-01 Faster sample rate confirmed.
2016-06-01 tons of bugfixes and bluetooth stabilizations battery indicators work! kind of. seems to be working i guess?
2016-06-01 minor changes to battery tests
2016-06-02 Badge should include extra data in advertising packet. Reworked battery updating.
2016-06-02 App now looks for voltage in broadcast message
2016-06-02 Adding voltage info from broadcast to python code
2016-06-04 Trying power samples for determining speech
2016-06-06 Added LED indicator server command.
2016-06-06 Badge prints MAC address to UART. Added script to retrieve MAC address.
2016-08-28 battery level stored+sent with scans
2016-08-28 Added voltage to proximity packs
2016-09-06 Generated new gerber files using PCB.ng CAM file. Made adjustments to CAM file to include milling layer and graphics
    [badge_03v4.bottom_copper.gbr, badge_03v4.bottom_mask.gbr, badge_03v4.bottom_paste.gbr, badge_03v4.bottom_silk.gbr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]
2016-09-08 RFduino code relocated to a new repository
    [RFDuino_badge.brd, RFDuino_badge.sch]
2016-09-19 Changed the code that reads from device_macs.txt to allow for lowercase mac addresses
2016-09-23 Printing exception to STDout
2016-10-01 Handing a case when there is only audio or only proximity data
2016-10-09 Changing init LED sequence to identify latest code
2016-10-13 added some printouts
2016-11-02 Added power LED to programmer. Gerber files
    [Badge_03v2-prog-2layer.brd, Badge_03v2-prog-2layer.sch]
2016-11-03 Add automatic test case runner
2016-11-03 Improved millis() implementation
2016-12-12 Sample more often but take fewer readings
2016-12-15 Improved battery sampling.
2016-12-21 New Startup LED animation
2017-06-14 Organizing directory structure
    [Badge_03v2-prog-2layer.GBL, Badge_03v2-prog-2layer.GBO, Badge_03v2-prog-2layer.GBP, Badge_03v2-prog-2layer.GBS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]
2017-07-25 Need to mount the app folder so temp files are accessible
2018-05-15 Scanner changes (#94)
    * Badge aggregates multiple RSSIs using max instead of mean. Closes #97
    * Badge keep room for several beacons in the scan. Closes #98
    * New LED startup sequence
2018-08-07 Badge 3v06 (#100)
    A new hardware version of the badge. Main changes:
    Accelerometer
    * Removed real-time clock and all components from the back of the badge
    * Removed button
    * New on/off switch (more pick&place friendly)
    * New battery holder
    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
    [badge_03v5.brd, badge_03v5.sch, badge_03v5_bom.csv, badge_03v5_bom_comparison_to_3v4.ods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]

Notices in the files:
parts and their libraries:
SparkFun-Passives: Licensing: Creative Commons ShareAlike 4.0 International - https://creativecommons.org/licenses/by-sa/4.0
